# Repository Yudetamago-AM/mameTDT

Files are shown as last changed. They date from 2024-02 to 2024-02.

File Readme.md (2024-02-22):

# mameTDT

**This is EXPERIMENTAL sensor for now.**

mameTDTは、TDT（Time Domain Transmissiometry）方式の誘電率センサーです。土の水分量や油の劣化度合いなど、用途に応じていろいろなものを測れます。
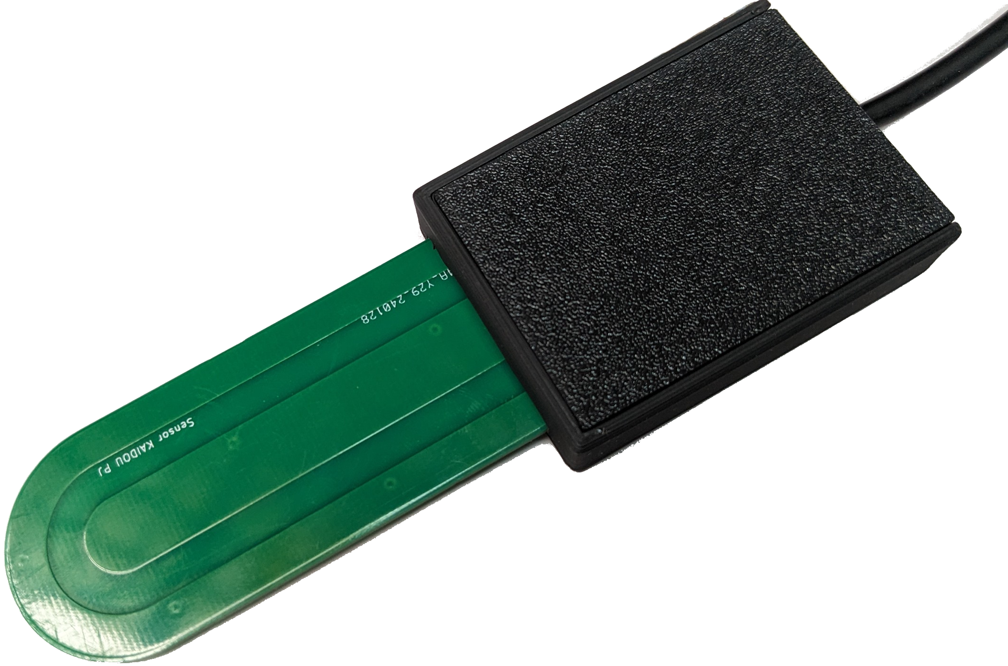
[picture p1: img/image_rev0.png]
rev0


以下フォルダの製造ファイルをJLCPCBなどの基板製造・実装業者に入稿すると、実装済み基板が送られてきます。本体とプローブ（先端）は別ファイルなので、気をつけてください。

[本体の製造ファイルはこちら](./pcb/tdc-tdt-kicad/jlcpcb/production_files/)  
[プローブ（30x70mm）の製造ファイルはこちら](./pcb/tdc-tdt-kicad/probe/standard_garber.zip)

## 原理
伝送路上の電磁波の伝播速度$`v[m/s]`$は、$`v=c/\sqrt{\epsilon}`$（光速$`c[m/s]`$、比誘電率$\epsilon$）で与えられます。これを変形すると、$`\epsilon=(c/v)^2`$です。つまり、伝播速度$v$がわかれば比誘電率$`\epsilon`$がわかります。

また、$`速度[m/s]=距離[m]/時間[s]`$という関係から、距離が一定で、時間がわかれば、速度がわかります。

以上から、一定の長さの伝送路の片端に適当に電圧（ステップ波、パルス波など）を加えて、もう片端に達するまでの時間を測れば、伝播速度がわかり、そこから比誘電率もわかります。

ここでは、TDC（Time to Digital Converter）という微少時間測定ICを使って伝播時間を測っています。

## 応用例
- 土壌水分量センサー

土が水・空気・土そのものの混合物だと考えると、誘電率がわかれば、水分量を知ることができます。
多くの場合、誘電率と水分量の関係は、Toppの式と呼ばれる下式で表されます。  

$`\theta=−5.3 × 10^{−2}  + 2.92 × 10^{−2} \epsilon−5.5 × 10^{−4} \epsilon^2+ 4.3 × 10^{−6}\epsilon^3`$  
ただし、土の水分量$`\theta [m^3/m^3]`$、比誘電率$`\epsilon`$です。

## 回路
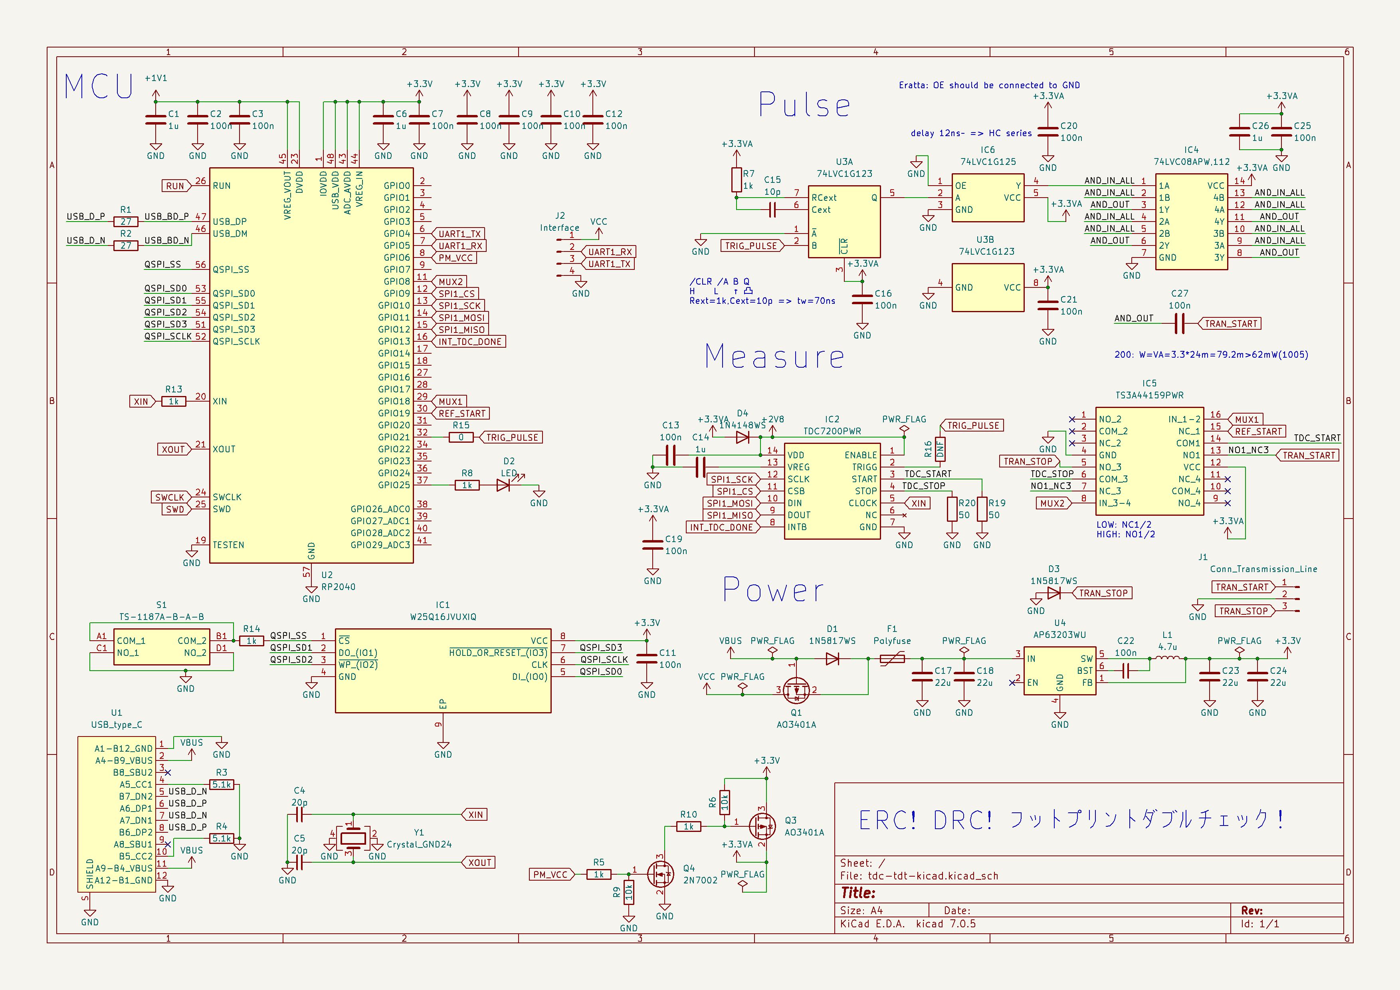
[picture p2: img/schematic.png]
schematic
 
回路図
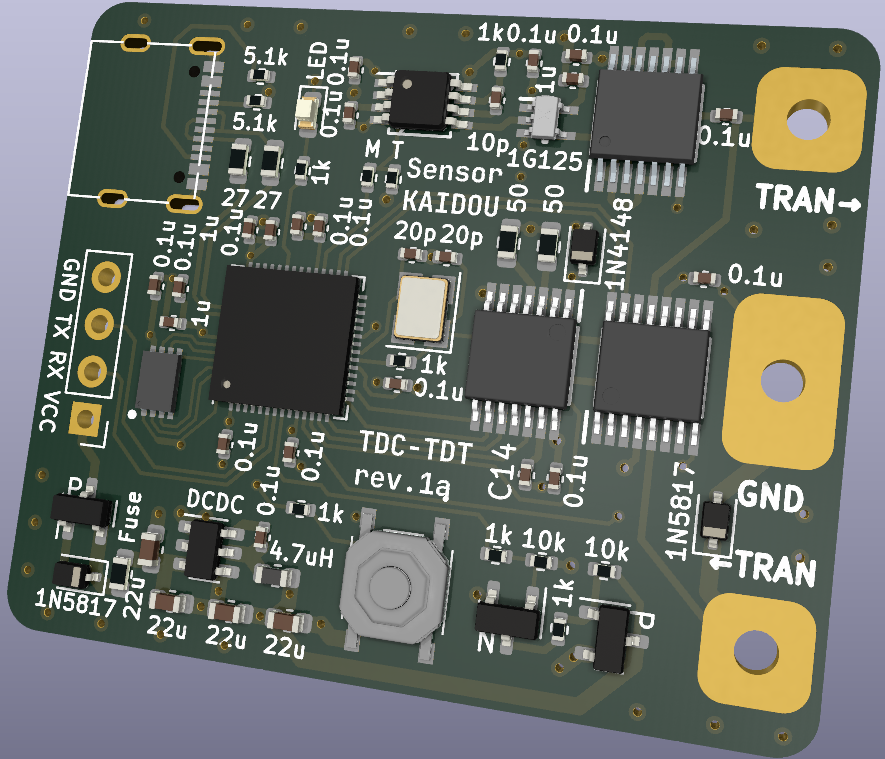
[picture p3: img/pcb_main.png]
pcb
  
PCBの3Dレンダリング
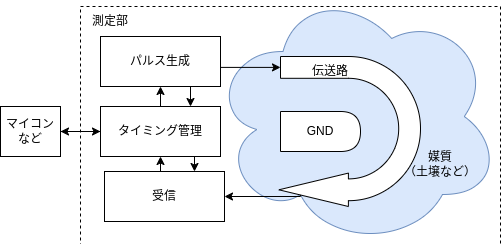
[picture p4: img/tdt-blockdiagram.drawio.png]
block
  
ブロック図

- パルス生成部  
単安定マルチバイブレータICの74LVC1G123で一定幅のパルス波を作り、バッファICで受けます。バッファICの出力をロジックIC（AND回路）の74LVC08APWに入力し、出力を４並列にして、ごく短い立ち上がり時間のパルス波を伝送路に入力します。十分な帯域幅を持ったオシロスコープがないので、確認出来ていませんが、おそらく500psくらいの立ち上がり時間です。

- タイミング管理部・受信部  
TDC7200というTI製のTDC ICを用いています。これは、測定できる最小時間が12nsですが、マイコンから基準開始信号を入力して、その基準からの時間の差を測って、12nsよりも短い時間を測っています。TIのアプリケーションレポートSNAA288を参考にしました。

- 電源回路  
Diodes IncのDCDCコンバータを使っています。USBと外部電源が同時に入力された場合、電圧の高い方を優先します。なお、入力電圧範囲は、4.5V～30Vを推奨します。

- マイコン  
Raspberry Pi財団の作ったマイコンRP2040を使っています。USBでのファームウェア書き込みが容易なことと、PIOというプログラム可能入出力機能が実装上便利だったので、採用しました。

## 使い方

### プログラムの書き込み
1. ここからファームウェアをダウンロードする。  
    （必要があれば、"Getting Started With Raspberry Pi Pico"などを参考に環境構築し、ビルドしてください）
1. 基板上のボタンを押しながら、USBでコンピュータに接続する。
1. USBメモリと同じように、RPI-RP2というドライブが認識されるので、ファームウェアをドラッグアンドドロップする。
1. 完了

### インターフェイス
UARTとUSBに対応しています。ケースに入れる際は、UARTのみの対応です。基板上の印字に従って配線し、適当なシリアル変換器や対応デバイスに接続してご利用ください。

### コマンド
現状、ASCIIコードの't'が入力された際、生の測定値（最大周波数：50Hz程度）を返します。適宜ノイズ処理を行ってご利用ください。

### 校正
少なくとも4点程度での校正をおすすめします。現状、生の値とプローブ長から決まる真値からExcel等で多項式補完して校正曲線を求める方法をおすすめします。校正に使いやすい物質とその比誘電率は次の通りです。

| 物質                     | 比誘電率(温度) | 
| ------------------------ | -------------- | 
| 空気                     | 1              | 
| イソプロパノール         | 19.92(25)      | 
| エタノール70wt%・水30wt% | 39.14(20)      | 
| エタノール40wt%・水60wt% | 56.49(20)      | 
| 水                       | 78.55(25)      | 

## ToDo
- 自動校正機能（プログラム）
- SDI-12への対応（プログラム）

## License
Apache-2.0 License

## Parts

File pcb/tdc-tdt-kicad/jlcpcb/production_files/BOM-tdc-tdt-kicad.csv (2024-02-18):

Comment | Designator | Footprint | LCSC
4.7u | L1 | L_0603_1608Metric | C1034
1k | R10,R13,R14,R5,R7,R8 | R_0402_1005Metric | C11702
74LVC1G125 | IC6 | SOT65P212X110-5N | C12519
AO3401A | Q1,Q3 | SOT-23 | C15127
TS3A44159PWR | IC5 | SOP65P640X120-16N | C151886
100n | C10,C11,C12,C13,C16,C19,C2,C20,C21,C22,C25,C27,C3,C7,C8,C9 | C_0402_1005Metric | C1525
20p | C4,C5 | C_0402_1005Metric | C1554
0 | R15 | R_0402_1005Metric | C17168
1N5817WS | D1,D3 | D_SOD-323 | C191023
RP2040 | U2 | QFN-56-1EP_7x7mm_P0.4mm_EP3.2x3.2mm | C2040
Polyfuse | F1 | Fuse_0603_1608Metric | C21189
1N4148WS | D4 | D_SOD-323 | C2128
50 | R19,R20 | R_0603_1608Metric | C22843
LED | D2 | LED_0603_1608Metric | C2286
10k | R6,R9 | R_0402_1005Metric | C25744
5.1k | R3,R4 | R_0402_1005Metric | C25905
TDC7200PWR | IC2 | SOP65P640X120-14N | C2653139
W25Q16JVUXIQ | IC1 | SON50P300X200X60-9N | C2843335
USB_type_C | U1 | USB_type_C | C2874568
TS-1187A-B-A-B | S1 | TS1187ABAB | C318884
10p | C15 | C_0402_1005Metric | C32949
27 | R1,R2 | R_0603_1608Metric | C4275
74LVC1G123 | U3 | TSSOP-8_3x3mm_P0.65mm | C513291
1u | C1,C14,C26,C6 | C_0402_1005Metric | C52923
22u | C17,C18,C23,C24 | C_0603_1608Metric | C59461
74LVC08APW,112 | IC4 | SOP65P640X110-14N | C6053
AP63203WU | U4 | TSOT-23-6 | C780769
2N7002 | Q4 | SOT-23 | C8545
Crystal_GND24 | Y1 | Crystal_SMD_3225-4Pin_3.2x2.5mm | C9002
Interface | J2 | PinHeader_1x04_P2.54mm_Vertical
Conn_Transmission_Line | J1 | conn_transmission_line
DNF | R16 | R_0402_1005Metric

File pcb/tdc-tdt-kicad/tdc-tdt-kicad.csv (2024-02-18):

# | Reference | Qty | Value | Footprint | DNP
1 | C1, C6, C26 | 3 | 1u | Capacitor_SMD:C_0402_1005Metric
2 | C2, C3, C7, C8, C9, C10, C11, C12, C13, C16, C19, C20, C21, C22, C25 | 15 | 100n | Capacitor_SMD:C_0402_1005Metric
3 | C4, C5 | 2 | 30p | Capacitor_SMD:C_0402_1005Metric
4 | C14 | 1 | 1u | Capacitor_SMD:C_0603_1608Metric
5 | C15 | 1 | 10p | Capacitor_SMD:C_0402_1005Metric
6 | C17, C18, C23, C24 | 4 | 22u | Capacitor_SMD:C_0603_1608Metric
7 | D1, D3 | 2 | CUS10S30,H3F | SamacSys_Parts:1SS357TPH3F
8 | D2 | 1 | LED | LED_SMD:LED_0603_1608Metric
9 | F1 | 1 | Polyfuse | Fuse:Fuse_0603_1608Metric
10 | IC1 | 1 | W25Q16JVUXIQ | SamacSys_Parts:SON50P300X200X60-9N
11 | IC2 | 1 | TDC7200PWR | SamacSys_Parts:SOP65P640X120-14N
12 | IC4 | 1 | 74LVC08APW,112 | SamacSys_Parts:SOP65P640X110-14N
13 | IC5 | 1 | TS3A44159PWR | SamacSys_Parts:SOP65P640X120-16N
14 | IC6 | 1 | 74HC1G126GW,125 | SamacSys_Parts:SOT65P212X110-5N
15 | J1 | 1 | Conn_Transmission_Line | tdc-tdt-lib:conn_transmission_line
16 | J2 | 1 | Interface | Connector_PinHeader_2.54mm:PinHeader_1x04_P2.54mm_Vertical
17 | L1 | 1 | 4.7u | Inductor_SMD:L_0603_1608Metric
18 | Q1, Q2 | 2 | IRLML6402 | SamacSys_Parts:SOT95P237X112-3N
19 | R1, R2 | 2 | 27 | Resistor_SMD:R_0402_1005Metric
20 | R3, R4 | 2 | 5.1k | Resistor_SMD:R_0402_1005Metric
21 | R5, R7, R8, R13, R14 | 5 | 1k | Resistor_SMD:R_0402_1005Metric
22 | R6 | 1 | 30k | Resistor_SMD:R_0402_1005Metric
23 | R9, R10, R11, R12 | 4 | 200 | Resistor_SMD:R_0603_1608Metric
24 | R15, R16 | 2 | 0 | Resistor_SMD:R_0402_1005Metric
25 | R17, R18 | 2 | 50 | Resistor_SMD:R_0402_1005Metric
26 | R19, R20 | 2 | 50 | Resistor_SMD:R_0603_1608Metric
27 | S1, S2 | 2 | SKRPACE010 | SamacSys_Parts:SMT_4.2X3.2_
28 | U1 | 1 | USB_type_C | tdc-tdt-lib:USB_type_C
29 | U2 | 1 | RP2040 | Package_DFN_QFN:QFN-56-1EP_7x7mm_P0.4mm_EP3.2x3.2mm
30 | U3 | 1 | 74LVC1G123 | Package_SO:TSSOP-8_3x3mm_P0.65mm
31 | U4 | 1 | AP63203WU | Package_TO_SOT_SMD:TSOT-23-6
32 | Y1 | 1 | Crystal_GND24 | Crystal:Crystal_SMD_3225-4Pin_3.2x2.5mm

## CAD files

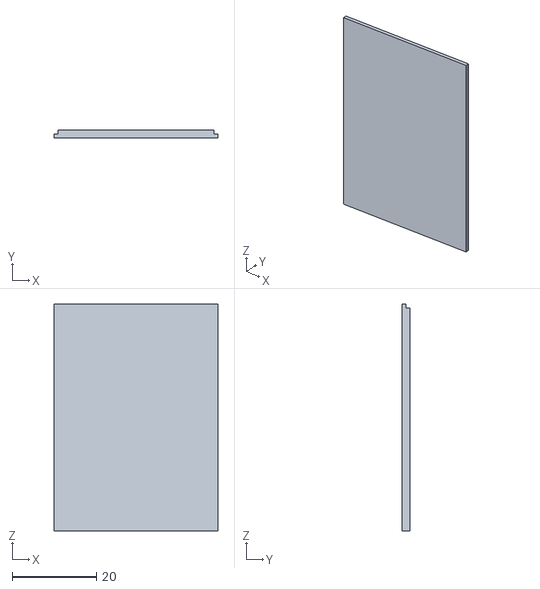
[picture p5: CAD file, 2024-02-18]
housing/case_top.stl
39.0 x 2.00 x 54.0

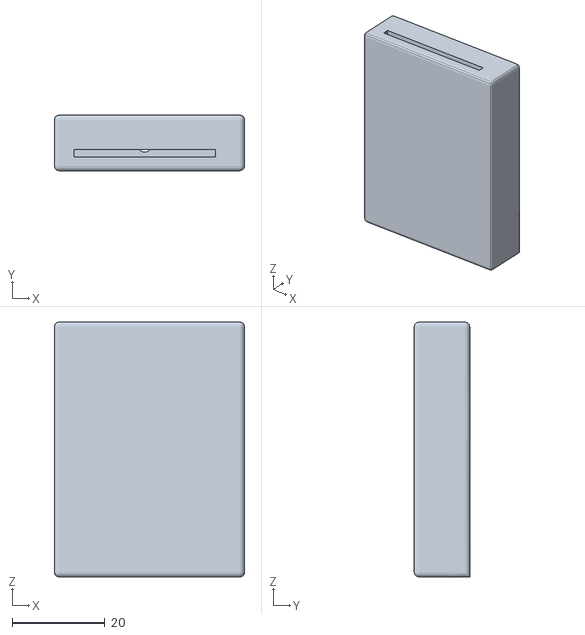
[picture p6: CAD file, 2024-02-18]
housing/case_basic.stl
41.0 x 12.0 x 55.0

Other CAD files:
housing/case_basic.ipt
housing/case_top.ipt

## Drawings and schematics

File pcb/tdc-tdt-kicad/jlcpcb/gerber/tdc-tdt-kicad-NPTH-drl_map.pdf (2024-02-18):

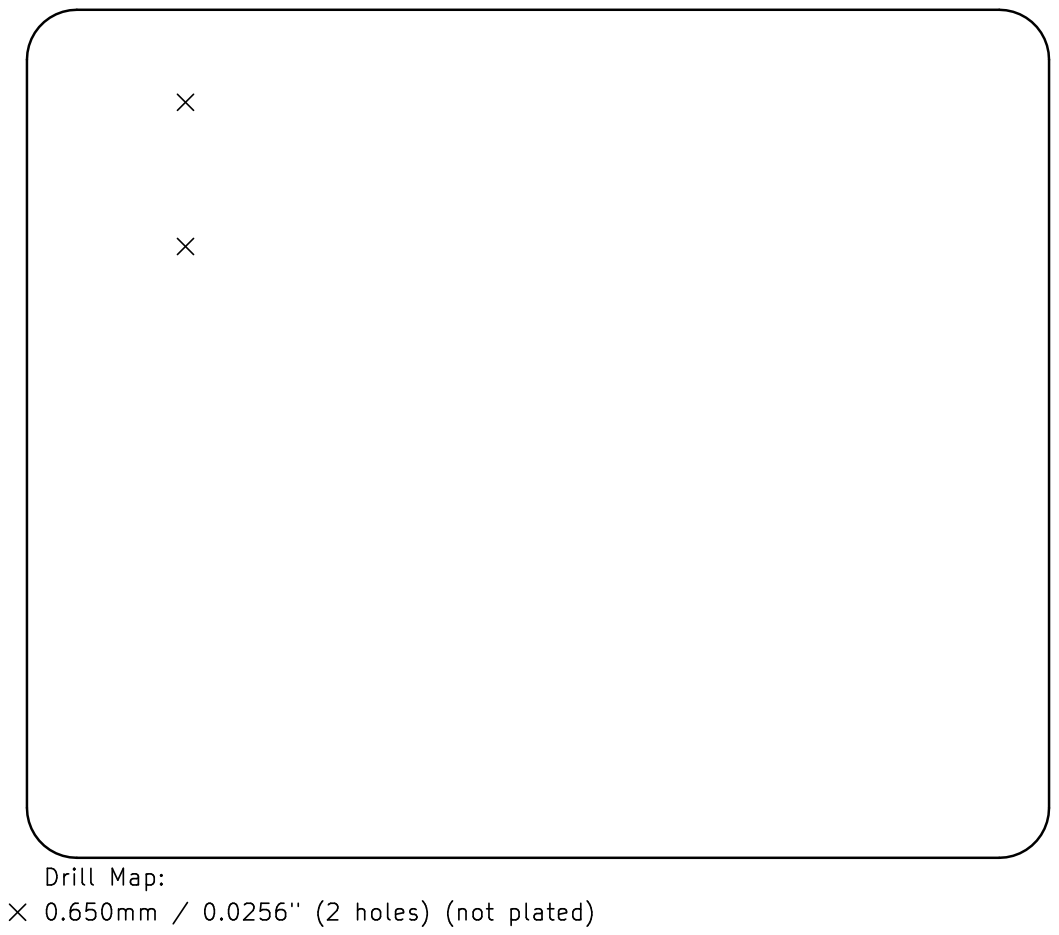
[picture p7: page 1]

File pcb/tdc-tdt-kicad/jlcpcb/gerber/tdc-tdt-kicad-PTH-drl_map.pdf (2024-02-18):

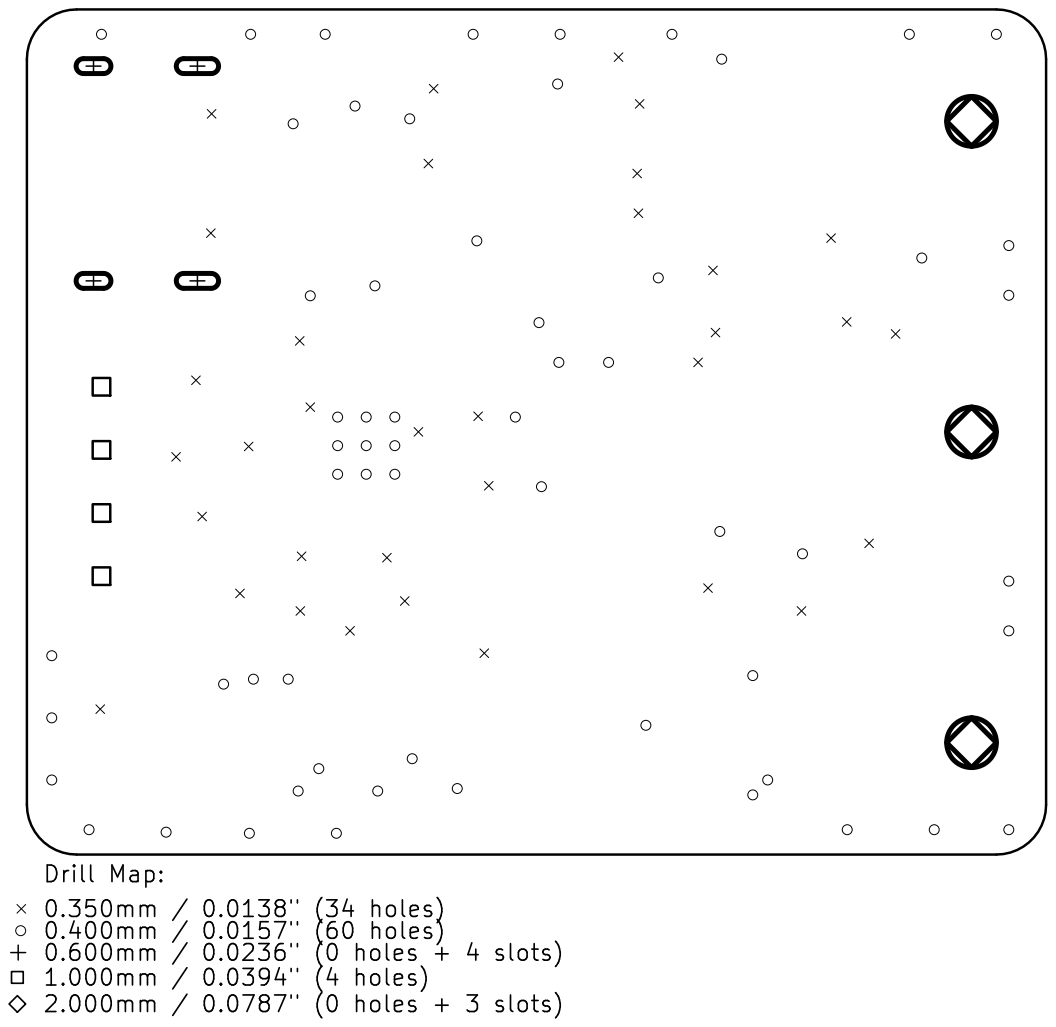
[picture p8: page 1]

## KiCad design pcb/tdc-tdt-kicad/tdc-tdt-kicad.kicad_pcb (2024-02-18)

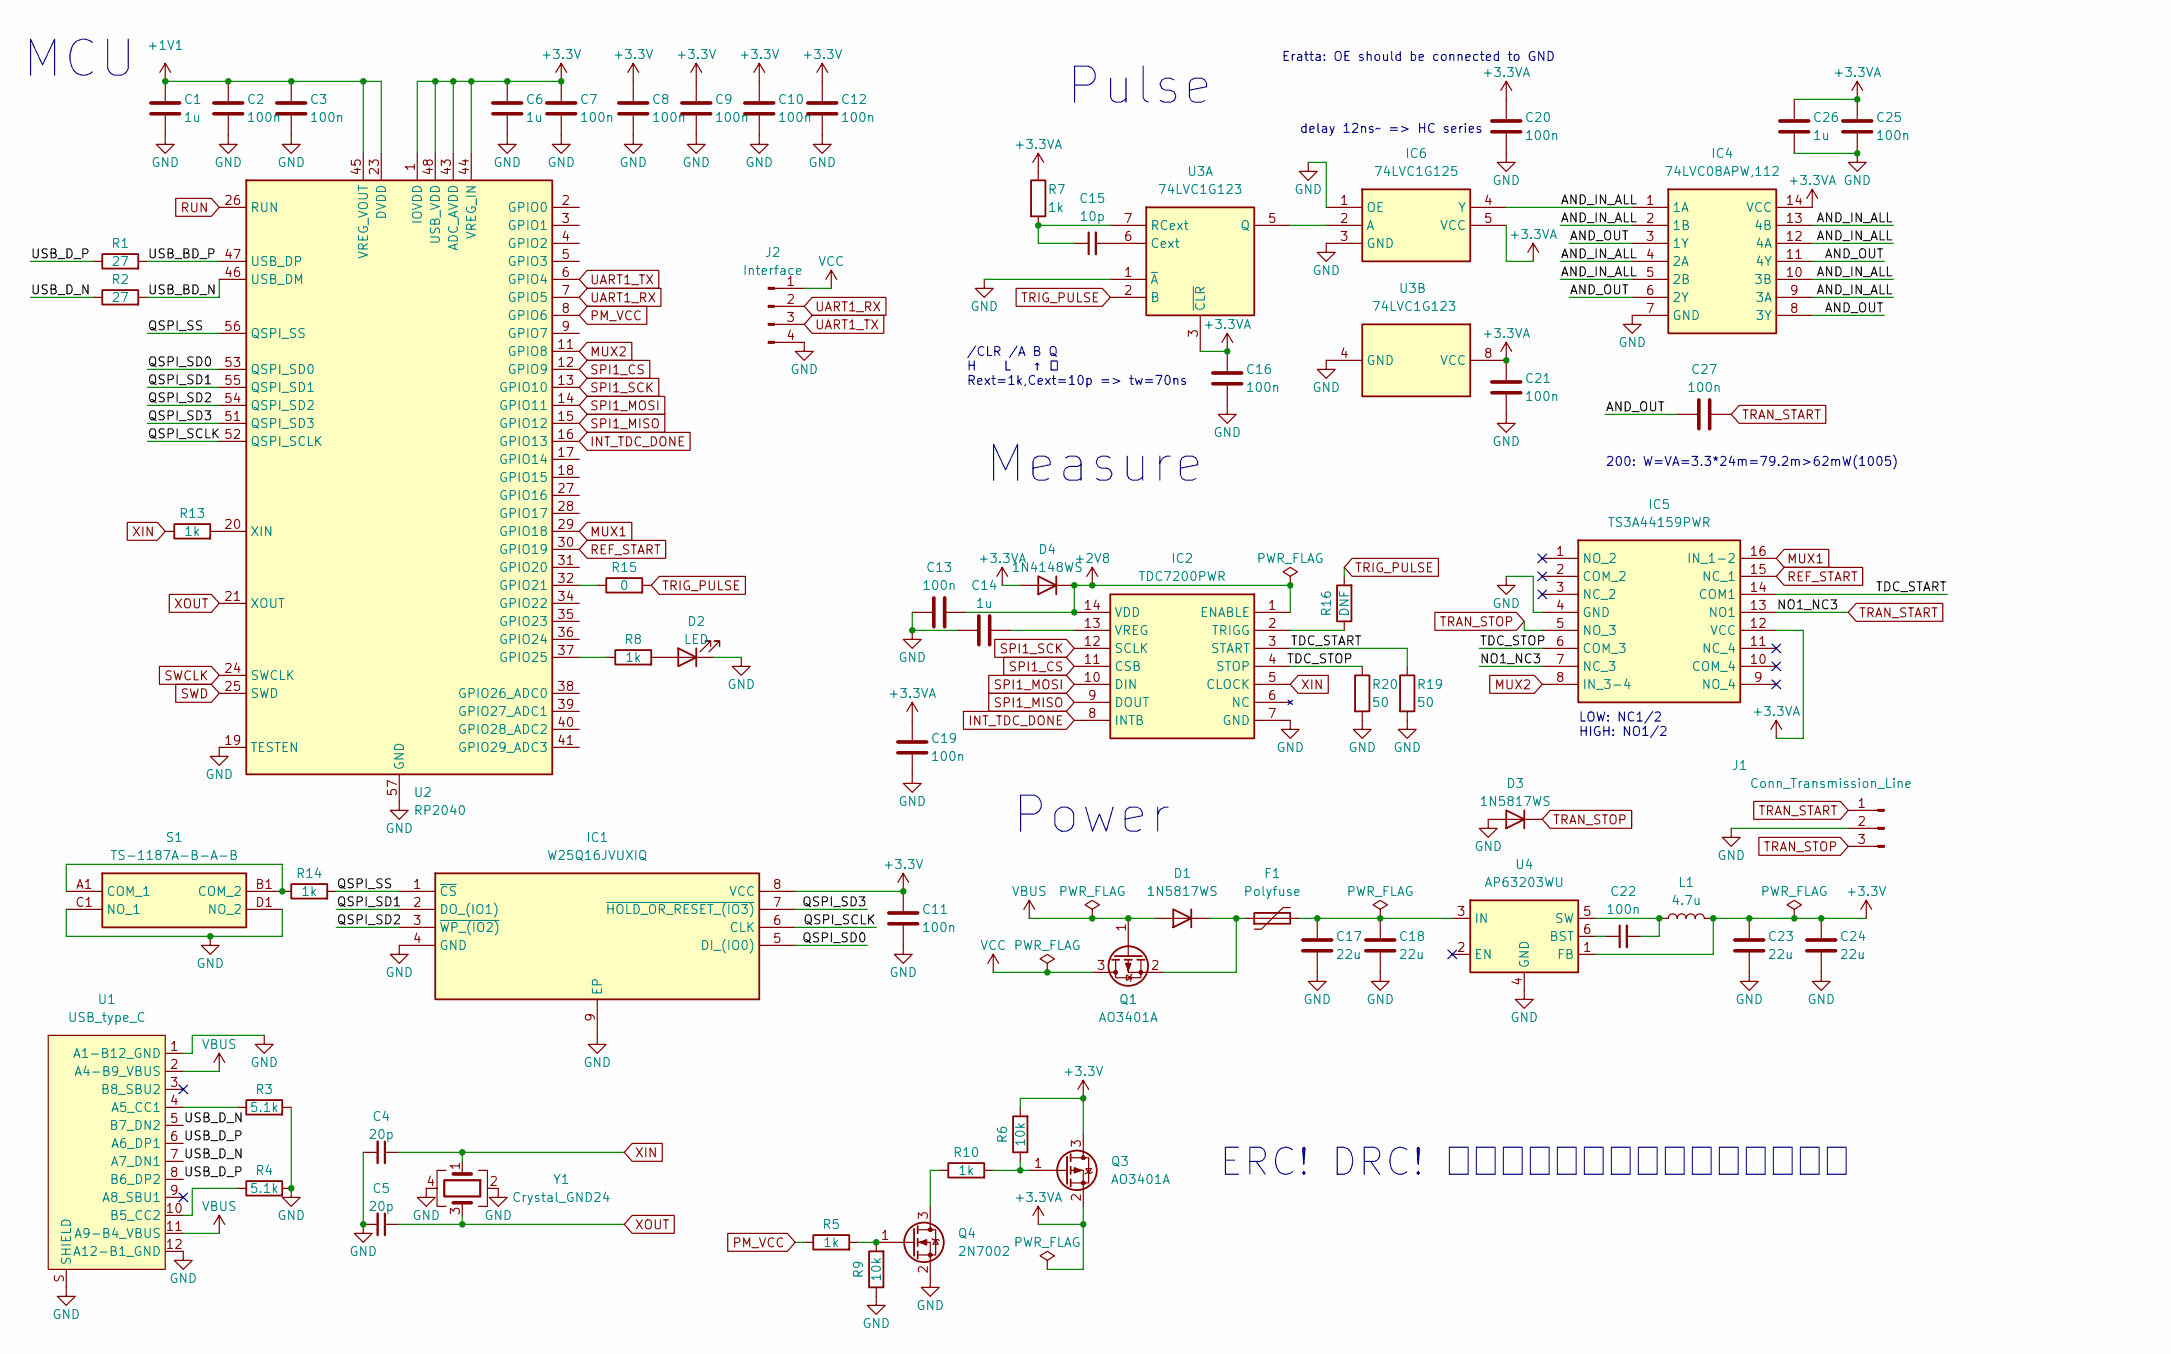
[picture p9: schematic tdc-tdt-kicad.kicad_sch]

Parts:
C1, C6, C14, C26: 1u; C_0402_1005Metric
C2, C3, C7, C8, C9, C10, C11, C12, C13, C16, C19, C20, C21, C22, C25, C27: 100n; C_0402_1005Metric
C4, C5: 20p; C_0402_1005Metric
C15: 10p; C_0402_1005Metric
C17, C18, C23, C24: 22u; C_0603_1608Metric
D1, D3: 1N5817WS; D_SOD-323
D2: LED; LED_0603_1608Metric
D4: 1N4148WS; D_SOD-323
F1: Polyfuse; Fuse_0603_1608Metric
IC1: W25Q16JVUXIQ; SON50P300X200X60-9N; Manufacturer_Part_Number W25Q16JVUXIQ
IC2: TDC7200PWR; SOP65P640X120-14N; Manufacturer_Part_Number TDC7200PWR; Mouser Part Number 595-TDC7200PWR
IC4: 74LVC08APW,112; SOP65P640X110-14N; Manufacturer_Part_Number 74LVC08APW,112; Mouser Part Number 771-74LVC08APW
IC5: TS3A44159PWR; SOP65P640X120-16N; Manufacturer_Part_Number TS3A44159PWR; Mouser Part Number 595-TS3A44159PWR
IC6: 74LVC1G125; SOT65P212X110-5N; Manufacturer_Part_Number 74HC1G126GW,125; Mouser Part Number 771-HC1G126GW125
J1: Conn_Transmission_Line; conn_transmission_line
J2: Interface; PinHeader_1x04_P2.54mm_Vertical
L1: 4.7u; L_0603_1608Metric
Q1, Q3: AO3401A; SOT-23
Q4: 2N7002; SOT-23
R1, R2: 27; R_0603_1608Metric
R3, R4: 5.1k; R_0402_1005Metric
R5, R7, R8, R10, R13, R14: 1k; R_0402_1005Metric
R6, R9: 10k; R_0402_1005Metric
R15: 0; R_0402_1005Metric
R16: DNF; R_0402_1005Metric
R19, R20: 50; R_0603_1608Metric
S1: TS-1187A-B-A-B; TS1187ABAB; Manufacturer_Part_Number TS-1187A-B-A-B
U1: USB_type_C
U2: RP2040; QFN-56-1EP_7x7mm_P0.4mm_EP3.2x3.2mm
U3: 74LVC1G123; TSSOP-8_3x3mm_P0.65mm
U4: AP63203WU; TSOT-23-6
Y1: Crystal_GND24; Crystal_SMD_3225-4Pin_3.2x2.5mm

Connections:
+1V1: C1.1, C2.1, C3.1, U2.23 (DVDD), U2.45 (VREG_VOUT), U2.50 (DVDD)
+2V8: C13.2, D4.1 (K), IC2.1 (ENABLE), IC2.14 (VDD)
+3.3V: C6.1, C7.1, C8.1, C9.1, C10.1, C11.1, C12.1, C23.1, C24.1, IC1.8 (VCC), L1.2, Q3.3 (D), R6.2, U2.1 (IOVDD), U2.10 (IOVDD), U2.22 (IOVDD), U2.33 (IOVDD), U2.42 (IOVDD), U2.43 (ADC_AVDD), U2.44 (VREG_IN), U2.48 (USB_VDD), U2.49 (IOVDD), U4.1 (FB)
+3.3VA: C16.1, C19.1, C20.1, C21.1, C25.1, C26.1, D4.2 (A), IC4.14 (VCC), IC5.12 (VCC), IC6.5 (VCC), Q3.2 (S), R7.1, U3.3 (~CLR), U3.8 (VCC)
/AND_IN_ALL: IC4.1 (1A), IC4.2 (1B), IC4.4 (2A), IC4.5 (2B), IC4.9 (3A), IC4.10 (3B), IC4.12 (4A), IC4.13 (4B), IC6.4 (Y)
/AND_OUT: C27.1, IC4.3 (1Y), IC4.6 (2Y), IC4.8 (3Y), IC4.11 (4Y)
/QSPI_SCLK: IC1.6 (CLK), U2.52 (QSPI_SCLK)
/QSPI_SD0: IC1.5 (DI_(IO0)), U2.53 (QSPI_SD0)
/QSPI_SD1: IC1.2 (DO_(IO1)), U2.55 (QSPI_SD1)
/QSPI_SD2: IC1.3 (~WP_(IO2)), U2.54 (QSPI_SD2)
/QSPI_SD3: IC1.7 (~HOLD_OR_RESET_(IO3)), U2.51 (QSPI_SD3)
/QSPI_SS: IC1.1 (~CS), R14.2, U2.56 (QSPI_SS)
/TDC_START: IC2.3 (START), IC5.14 (COM1), R19.1
/TDC_STOP: IC2.4 (STOP), IC5.6 (COM_3), R20.1
/USB_BD_N: R2.2, U2.46 (USB_DM)
/USB_BD_P: R1.2, U2.47 (USB_DP)
/USB_D_N: R2.1, U1.5 (B7_DN2), U1.7 (A7_DN1)
/USB_D_P: R1.1, U1.6 (A6_DP1), U1.8 (B6_DP2)
GND: C1.2, C2.2, C3.2, C4.2, C5.2, C6.2, C7.2, C8.2, C9.2, C10.2, C11.2, C12.2, C13.1, C14.1, C16.2, C17.2, C18.2, C19.2, C20.2, C21.2, C23.2, C24.2, C25.2, C26.2, D2.1 (K), D3.2 (A), IC1.4 (GND), IC1.9 (EP), IC2.7 (GND), IC4.7 (GND), IC5.4 (GND), IC6.1 (OE), IC6.3 (GND), J1.2, J2.4, Q4.2 (S), R3.2, R4.2, R9.1, R19.2, R20.2, S1.C1 (NO_1), S1.D1 (NO_2), U1.1 (A1-B12_GND), U1.12 (A12-B1_GND), U1.S (SHIELD), U2.19 (TESTEN), U2.57 (GND), U3.1 (~A), U3.4 (GND), U4.4 (GND), Y1.2, Y1.4
INT_TDC_DONE: IC2.8 (INTB), U2.16 (GPIO13)
MUX1: IC5.16 (IN_1-2), U2.29 (GPIO18)
MUX2: IC5.8 (IN_3-4), U2.11 (GPIO8)
unnamed: D1.1 (K), F1.1, Q1.2 (S)
unnamed: D2.2 (A), R8.2
unnamed: IC2.2 (TRIGG), R16.1
unnamed: C14.2, IC2.13 (VREG)
unnamed: IC6.2 (A), U3.5 (Q)
unnamed: Q3.1 (G), R6.1, R10.2
unnamed: Q4.3 (D), R10.1
unnamed: Q4.1 (G), R5.2, R9.2
unnamed: R14.1, S1.A1 (COM_1), S1.B1 (COM_2)
unnamed: R3.1, U1.4 (A5_CC1)
unnamed: R4.1, U1.10 (B5_CC2)
unnamed: R15.1, U2.32 (GPIO21)
unnamed: R8.1, U2.37 (GPIO25)
unnamed: R13.2, U2.20 (XIN)
unnamed: C15.2, U3.6 (Cext)
unnamed: C15.1, R7.2, U3.7 (RCext)
unnamed: C22.1, U4.6 (BST)
unnamed: C17.1, C18.1, F1.2, U4.3 (IN)
unnamed: C22.2, L1.1, U4.5 (SW)
PM_VCC: R5.1, U2.8 (GPIO6)
REF_START: IC5.15 (NC_1), U2.30 (GPIO19)
RUN: U2.26 (RUN)
SPI1_CS: IC2.11 (CSB), U2.12 (GPIO9)
SPI1_MISO: IC2.9 (DOUT), U2.15 (GPIO12)
SPI1_MOSI: IC2.10 (DIN), U2.14 (GPIO11)
SPI1_SCK: IC2.12 (SCLK), U2.13 (GPIO10)
SWCLK: U2.24 (SWCLK)
SWD: U2.25 (SWD)
TRAN_START: C27.2, IC5.7 (NC_3), IC5.13 (NO1), J1.1
TRAN_STOP: D3.1 (K), IC5.5 (NO_3), J1.3
TRIG_PULSE: R15.2, R16.2, U3.2 (B)
UART1_RX: J2.2, U2.7 (GPIO5)
UART1_TX: J2.3, U2.6 (GPIO4)
VBUS: D1.2 (A), Q1.1 (G), U1.2 (A4-B9_VBUS), U1.11 (A9-B4_VBUS)
VCC: J2.1, Q1.3 (D)
XIN: C4.1, IC2.5 (CLOCK), R13.1, Y1.1
XOUT: C5.1, U2.21 (XOUT), Y1.3

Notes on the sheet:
LOW: NC1/2 HIGH: NO1/2
200: W=VA=3.3*24m=79.2m>62mW(1005)
Pulse
Power
delay 12ns~ => HC series
ERC! DRC! フットプリントダブルチェック！
MCU
/CLR /A B Q H L ↑ 凸 Rext=1k,Cext=10p => tw=70ns
Eratta: OE should be connected to GND
Measure

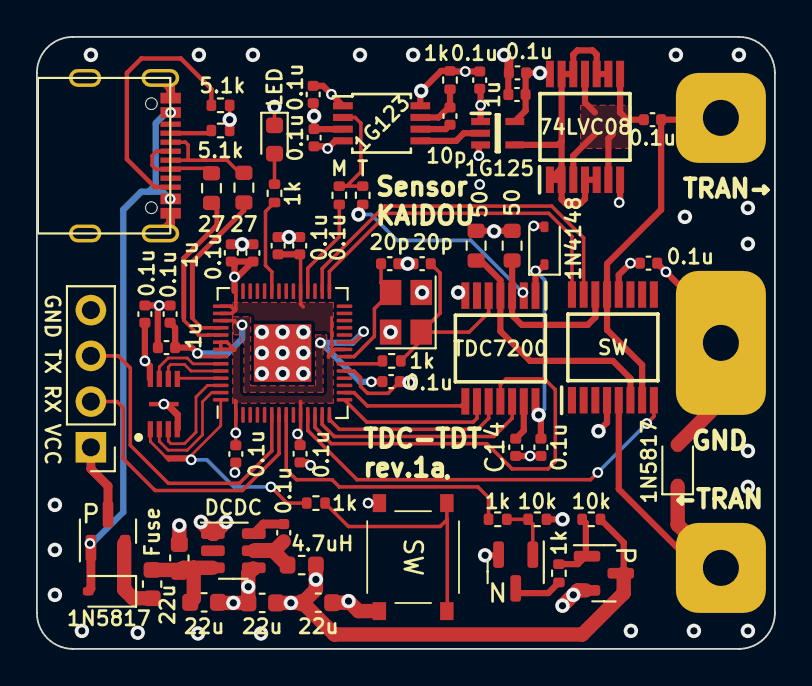
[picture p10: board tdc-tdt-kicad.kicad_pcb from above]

Board: 4 copper layers, 41.0 x 34.0 mm, 65 parts (0 on the bottom side), 56 nets.

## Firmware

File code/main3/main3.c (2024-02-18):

#include <stdint.h>
#include <stdio.h>
#include "hardware/timer.h"
#include "pico/stdlib.h"
#include "hardware/pio.h"
#include "hardware/spi.h"
#include "pio_out.pio.h"

#define abs(x) (((x)<0)?(-(x)):(x))

const uint8_t pin_mux1 = 18; // LOW: REF_START, HIGH: TRAN_START
const uint8_t pin_mux2 = 8; // LOW: TRAN_START, HIGH: TRAN_STOP
const uint8_t pin_ref_start = 19;
const uint8_t pin_trig_pulse = 21; // Rising edge: Trigger pulse
const uint8_t pin_mes_vcc = 6; // LOW: ON, HIGH: OFF
const uint8_t pin_int_tdc = 13; // HIGH: data ready, LOW: else

const uint8_t pin_spi1_cs = 9; // Active LOW
const uint8_t pin_spi1_sck = 10;
const uint8_t pin_spi1_mosi = 11;
const uint8_t pin_spi1_miso = 12;

enum tdc_mode {
	RISE_RISE = 0b10000001,
	RISE_FALL = 0b10010001,
	FALL_RISE = 0b10001001,
	FALL_FALL = 0b10011001,
};

uint32_t readData(uint8_t addr) {
	uint8_t buf[3] = {0};
	gpio_put(pin_spi1_cs, 0);
	asm volatile("nop \n nop \n nop");
	spi_write_blocking(spi1, &addr, 1);
	spi_read_blocking(spi1, 0x00, buf, 3);
	asm volatile("nop");
	gpio_put(pin_spi1_cs, 1);
	return ((buf[0] << 16) | (buf[1] << 8) | buf[2]);
}

double measure(PIO pio, uint8_t sm, enum tdc_mode mode) {
	uint8_t wbuf[2] = {0};
	//    uint32_t time_before = time_us_32(), time_after;
	//    printf("trigg. %d ms, ", time_before / 1000);

	// start generating pulse by PIO
	pio_sm_set_enabled(pio, sm, true);

	// start measuring in TDC
	gpio_put(pin_spi1_cs, 0);
	asm volatile("nop \n nop \n nop");
	wbuf[0] = 0b01000000; // Write Reg 0x00
						  //  wbuf[1] = 0b10000001; // Mode 1, START: Rising, STOP: Rising Edge
						  //	wbuf[1] = 0b10010001; // Mode 1, START: Rising, STOP: Falling Edge
						  //  wbuf[1] = 0b10011001; // Mode 1, START: Falling, STOP: Falling Edge
						  //  wbuf[1] = 0b10001001; // Mode 1, START: Falling, STOP: Rising Edge
						  //	wbuf[2] = 0b01111000; // 128 times averaging(should be auto incrementing enabled)
	wbuf[1] = mode;
	spi_write_blocking(spi1, wbuf, 2);
	asm volatile("nop");
	gpio_put(pin_spi1_cs, 1);

	//while (gpio_get(pin_int_tdc) == 0){tight_loop_contents();}
	sleep_us(2);
	//    printf("gpio_get(pin_int_tdc): %d\n", gpio_get(pin_int_tdc));

	// end generating pulse by PIO
	pio_sm_set_enabled(pio, sm, false);

	// read out data
	uint32_t time1 = readData(0x10);
	//    uint32_t clock_cnt1 = readData(0x11);
	uint32_t calib1 = readData(0x1b);
	uint32_t calib2 = readData(0x1c);
	double cal_count = (calib2 - calib1) / (10.0 - 1.0);
	double norm_LSB = 1 / (cal_count * 12.0 / 1000);
	//double tof1 = time1 * norm_LSB + clock_cnt1 * (1 / (12.0));
	double tof1 = time1 * norm_LSB;
	//   printf("tof: %f ns, elapsed: %d us\n", tof1, (time_us_32()-time_before));
	//printf("time1: %d, clock_cnt1: %d, calib1: %d, calib2: %d, cal_count: %f, norm_LSB: %f\n", time1, clock_cnt1, calib2, cal_count, norm_LSB);
	//   printf("time1: %d, calib1: %d, calib2: %d, cal_count: %f, norm_LSB: %f\n", time1, calib1, calib2, cal_count, norm_LSB);
	// 	time_after = time_us_32();
	//	printf("elapsed: %d us, ", time_after - time_before);

	return tof1;
}

double measure_avg256(PIO pio, uint8_t sm, uint8_t mux2, uint8_t mode) {
	double sum = 0.0, start = 0.0, stop = 0.0, diff = 0.0;
	printf("trigg. %d ms, mux2: 0x%x, mode: 0x%x ", time_us_32() / 1000, mux2, mode);
	printf("START: ");
	gpio_put(pin_mux2, (mux2>>1));
	asm volatile("nop");

	sum = 0;
	//			before = time_us_32();
	for (int8_t i = 0; i < 64; i++) sum += measure(pio, sm, mode);
	for (int8_t i = 0; i < 64; i++) sum += measure(pio, sm, mode);
	for (int8_t i = 0; i < 64; i++) sum += measure(pio, sm, mode);
	for (int8_t i = 0; i < 64; i++) sum += measure(pio, sm, mode);
	//			after = time_us_32();
	//			printf("T: %d us, ", (after - before) / 64);
	start = sum / 256.0;

	printf("tof: %2.3f, ", start);
	printf("STOP: ");
	gpio_put(pin_mux2, (mux2&0x01));
	asm volatile("nop");

	sum = 0;
	for (int8_t i = 0; i < 64; i++) sum += measure(pio, sm, mode);
	for (int8_t i = 0; i < 64; i++) sum += measure(pio, sm, mode);
	for (int8_t i = 0; i < 64; i++) sum += measure(pio, sm, mode);
	for (int8_t i = 0; i < 64; i++) sum += measure(pio, sm, mode);
	stop = sum / 256.0;
	diff = stop - start;
	printf("tof: %2.3f, ", stop);
	printf("diff: %2.3f", diff);
	printf("\n");

	return diff;
}

int main(void) {
	stdio_init_all();
	sleep_ms(2000);
	printf("hello, this is main\n");

	//    gpio_init(pin_trig_pulse);
	//    gpio_set_dir(pin_trig_pulse, GPIO_OUT);
	//    gpio_put(pin_trig_pulse, 0); // no pulse

	gpio_init(pin_mes_vcc);
	gpio_set_dir(pin_mes_vcc, GPIO_OUT);
	gpio_put(pin_mes_vcc, 0); // on

	gpio_init(pin_mux1);
	gpio_set_dir(pin_mux1, GPIO_OUT);
	gpio_put(pin_mux1, 0); // REF_START

	gpio_init(pin_mux2);
	gpio_set_dir(pin_mux2, GPIO_OUT);
	gpio_put(pin_mux2, 0);

	//    gpio_init(pin_ref_start);
	//    gpio_set_dir(pin_ref_start, GPIO_OUT);
	//    gpio_put(pin_ref_start, 0);

	gpio_init(pin_int_tdc);
	gpio_set_dir(pin_int_tdc, GPIO_IN);

	gpio_init(pin_spi1_cs);
	gpio_set_dir(pin_spi1_cs, GPIO_OUT);
	gpio_put(pin_spi1_cs, 1); // Active LOW

	spi_init(spi1, 10 * 1000 * 1000); // 10MHz
	gpio_set_function(pin_spi1_miso, GPIO_FUNC_SPI);
	gpio_set_function(pin_spi1_sck, GPIO_FUNC_SPI);
	gpio_set_function(pin_spi1_mosi, GPIO_FUNC_SPI);

	uint8_t wbuf[2] = {0};
	gpio_put(pin_spi1_cs, 0);
	asm volatile("nop \n nop \n nop");
	wbuf[0] = 0b01000011; // Write Reg 0x03
	wbuf[1] = 0b00000111; // enable interrupt
	spi_write_blocking(spi1, wbuf, 3);
	asm volatile("nop");
	gpio_put(pin_spi1_cs, 1);
	//    gpio_put(pin_spi1_cs, 0);
	//    asm volatile("nop \n nop \n nop");
	//    wbuf[0] = 0b01000001; // Write Reg 0x01
	//    wbuf[1] = 0b01111000; // enable 128 times averaging
	//    spi_write_blocking(spi1, wbuf, 3);
	//    asm volatile("nop");
	//    gpio_put(pin_spi1_cs, 1);

	// PIO settings
	PIO pio = pio0;
	uint8_t offset = pio_add_program(pio, &pio_out_program);
	uint8_t sm = pio_claim_unused_sm(pio, true);
	pio_out_program_init(pio, sm, offset, pin_ref_start);

	char c = 0;
	while (1) {
		if ((c = getchar_timeout_us(10*1000)) == 't') {
			// A: stArt, O: stOp, R: Rise, F: Fall
			double mes_AA_RR = 0.0, mes_AA_FF = 0.0,
				   mes_OO_RR = 0.0, mes_OO_FF = 0.0;
			const double V_RR = 2.8;
			double V_FF = 0.5;

			// START to START: mux2==0b00
			// RISE to RISE
			mes_AA_RR = measure_avg256(pio, sm, 0b00, RISE_RISE);
			// FALL to FALL
			mes_AA_FF = measure_avg256(pio, sm, 0b00, FALL_FALL);

			// START to STOP: mux2==0b01
			// RISE to RISE
			mes_OO_RR = measure_avg256(pio, sm, 0b01, RISE_RISE);
			// FALL to FALL
			mes_OO_FF = measure_avg256(pio, sm, 0b01, FALL_FALL);

			double t_RR = mes_OO_RR - abs(mes_AA_RR);
			double t_FF = mes_OO_FF - abs(mes_AA_FF);

			// guess true propagation delay
			double x = (V_FF*t_RR - V_RR*t_FF) / (t_FF - t_RR);
			x = abs(x);
			double t_p = (t_FF * x) / (V_FF + x);
			printf("V_RR: %1.1f V_FF: %1.1f ", V_RR, V_FF);
			printf("x: %2.3f t_p: %2.3f\n", x, t_p);

		}
		//sleep_ms(1);
	}
}
